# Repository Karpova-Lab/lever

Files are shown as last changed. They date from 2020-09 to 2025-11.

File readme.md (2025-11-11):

# Retractable Lever

This repository contains design files for a retractable lever used in behavioral neuroscience experiments.

Full documentation can be found at https://karpova-lab.github.io/lever/

Feedback and questions can be submitted to [discussions](https://github.com/Karpova-Lab/lever/discussions).

demo gif
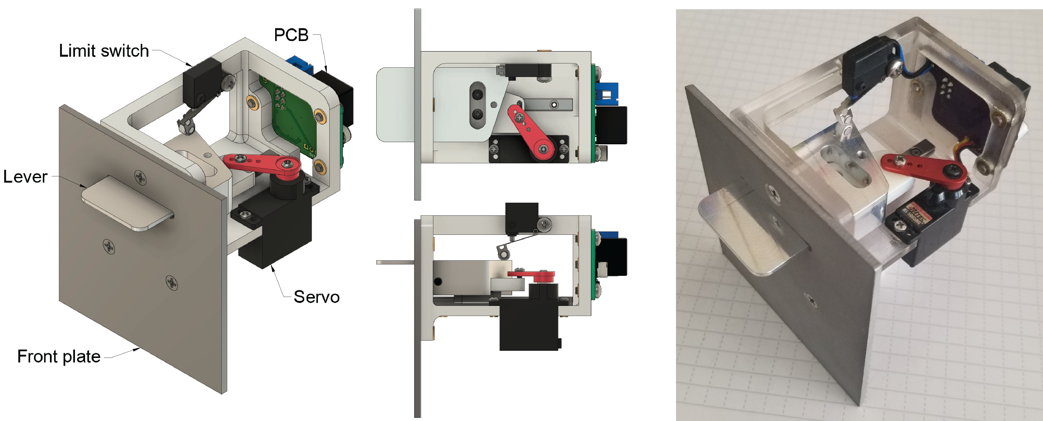
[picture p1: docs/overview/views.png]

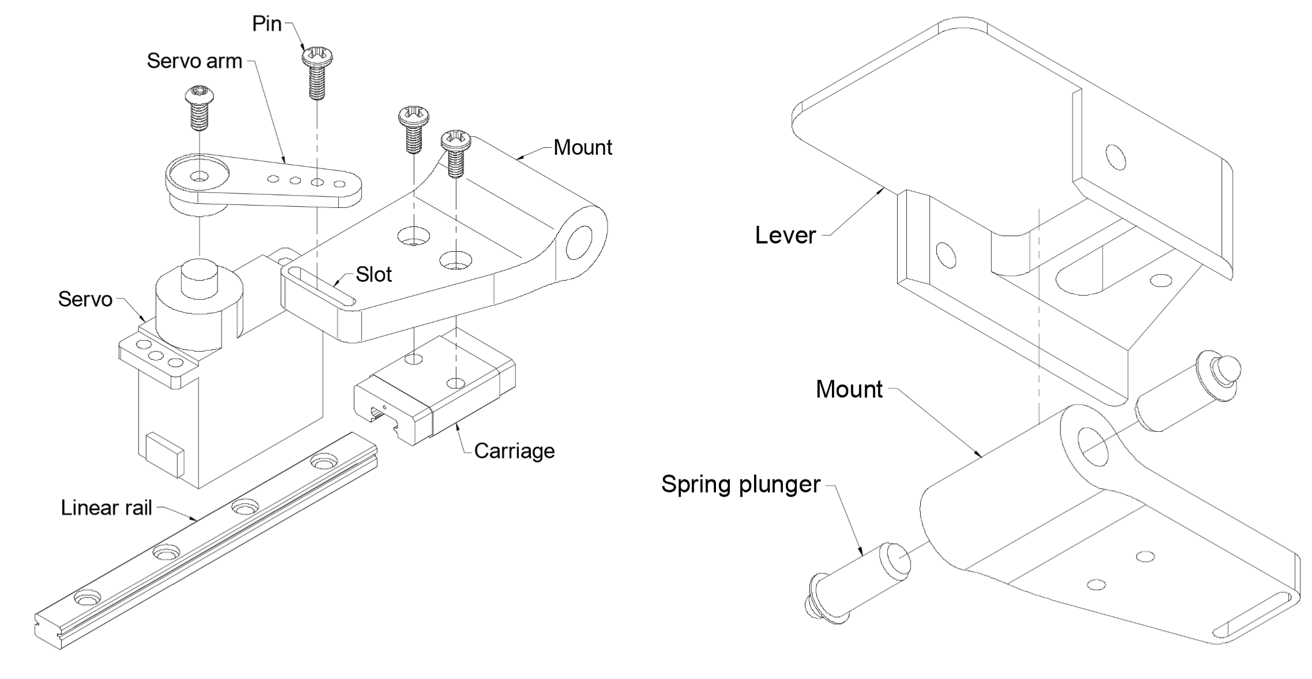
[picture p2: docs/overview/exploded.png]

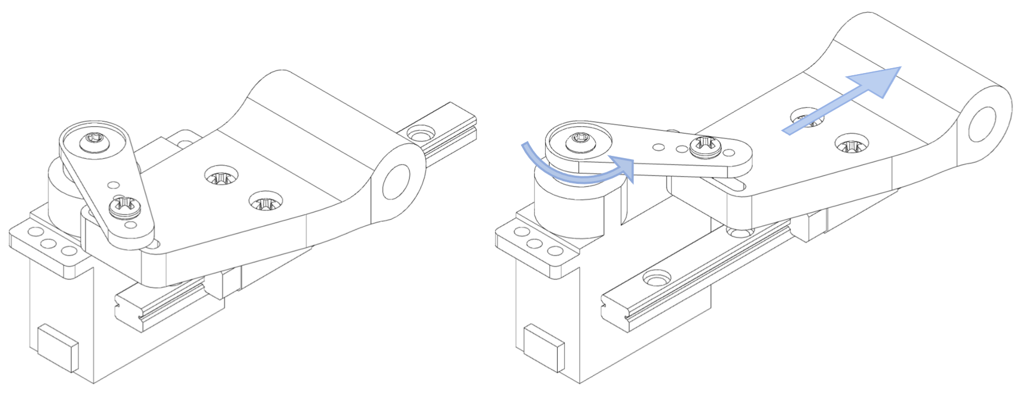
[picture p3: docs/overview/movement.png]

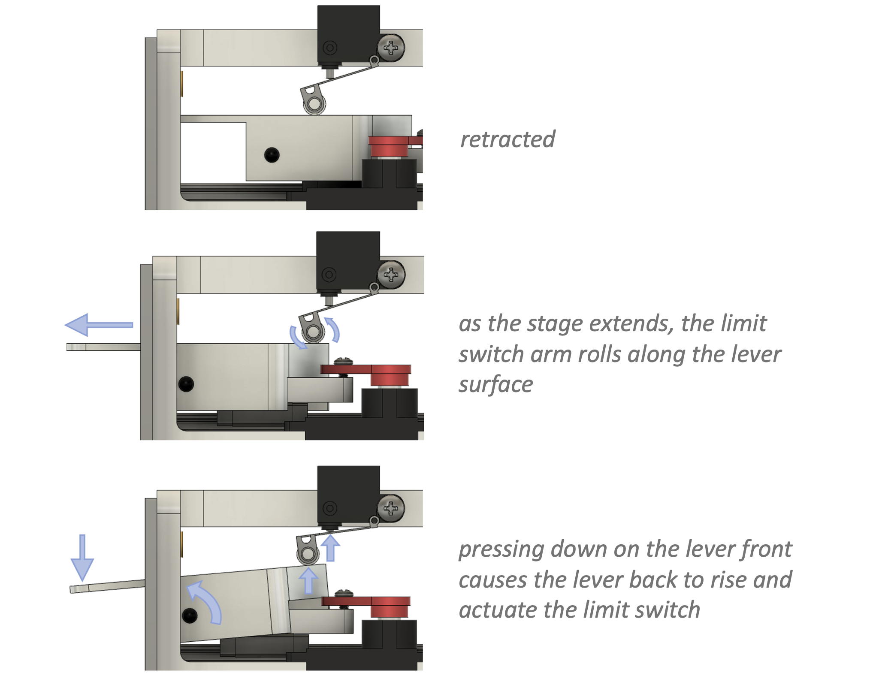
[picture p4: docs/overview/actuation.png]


## License
This project is licensed under the [Janelia open-source hardware license](license_hardare.txt) and [Janelia 3-term BSD open-source software license](license_software.txt).

Please contact [innovation@janelia.hhmi.org](mailto:innovation@janelia.hhmi.org) if you have any questions about licensing or would like to use this project commercially.

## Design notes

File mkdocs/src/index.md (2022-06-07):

# Overview



This is the documentation for building and using a retractable lever.

This project was developed by Andy Lustig in the [Karpova Lab](https://www.janelia.org/lab/karpova-lab) at HHMI's Janelia Research Campus.

## Features

- Receives an input signal to either extend or retract the lever
- Produces an output signal corresponding to the status of the lever (pressed or not pressed)
- [pyControl](https://pycontrol.readthedocs.io/en/latest/user-guide/hardware/#behaviour-ports) compatible
- Fast - 180ms to extend or retract
- Durable - faceplate and lever are made of aluminum and can hold up to abuse from rodent claws and teeth
- Open source - all files are available on [GitHub](https://github.com/Karpova-Lab/nosepoke) and can be modified to meet custom needs

## Diagrams

### Exploded views


<figcaption>(Left) The servo and lever mount interface using a pin and slot mechanism. (Right) The lever rotates about two spring plungers.</figcaption>

### Carriage movement

<figcaption>The rotation of the servo arm is translated into linear movement of the carriage along a guide rail</figcaption>

### Lever function


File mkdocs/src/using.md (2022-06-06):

# Using

## pyControl

This lever works with the [pyControl](https://pycontrol.readthedocs.io/en/latest/) behavior framework. 
Specifically, this means that the RJ45 [pinout](https://pycontrol.readthedocs.io/en/latest/user-guide/hardware/#behaviour-ports) is compatible with pyControl. 
Using an ethernet cable, you can connect the lever to an [original breakout board](https://open-ephys.org/pycontrol/pycontrol)  or a [D-series breakout board](https://karpova-lab.github.io/pyControl-D-Series-Breakout/index.html). 

## Example task

!!! info 
    For the example to work, [:material-file-download: lever_device.py](using/lever_device.py) must be downloaded and placed in your `devices` folder. 
    Then after connecting to you pyboard, use the "config" button to "Load framework".
    This will transfer the device files, including _lever.py, from your computer onto the pyboard microcontroller.

Below is an example task you can run to test the lever. 
The task assumes a lever is connected to **port 1** of your breakout board.

When the task starts, the lever will extend. 
Pressing the extended lever 3 times will cause the lever to retract.
After 1 second, the lever will extend again.
The number of presses required and the duration of the retraction are variables that can be adjusted.

``` python
from pyControl.utility import *
from devices import *
import pyControl.hardware as _h

## uncomment one of the following two lines depending out which breakout board you are using
board = Breakout_1_2()  # original pyboard breakout
# board = Breakout_dseries_1_6()  # d-series pyboard breakout

lever = Lever(board.port_1, lever_event="lever")

states = ["available", "retracted"]
events = ["lever", "extend_again"]

v.press_count___ = 0
v.retract_time_ms = 1000
v.required_presses = 3
initial_state = "available"

def available(event):
    if event == "entry":
        lever.extend()
        v.press_count___ = 0
    elif event == "lever":
        v.press_count___ += 1
        if v.press_count___ == v.required_presses:
            goto_state("retracted")

def retracted(event):
    if event == "entry":
        lever.retract()
        set_timer("extend_again", v.retract_time_ms)
    elif event == "extend_again":
        goto_state("available")
```

For more information on writing your own tasks, refer to the  [pyControl documentation](https://pycontrol.readthedocs.io/en/latest/user-guide/programming-tasks/).

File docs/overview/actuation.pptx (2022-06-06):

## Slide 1

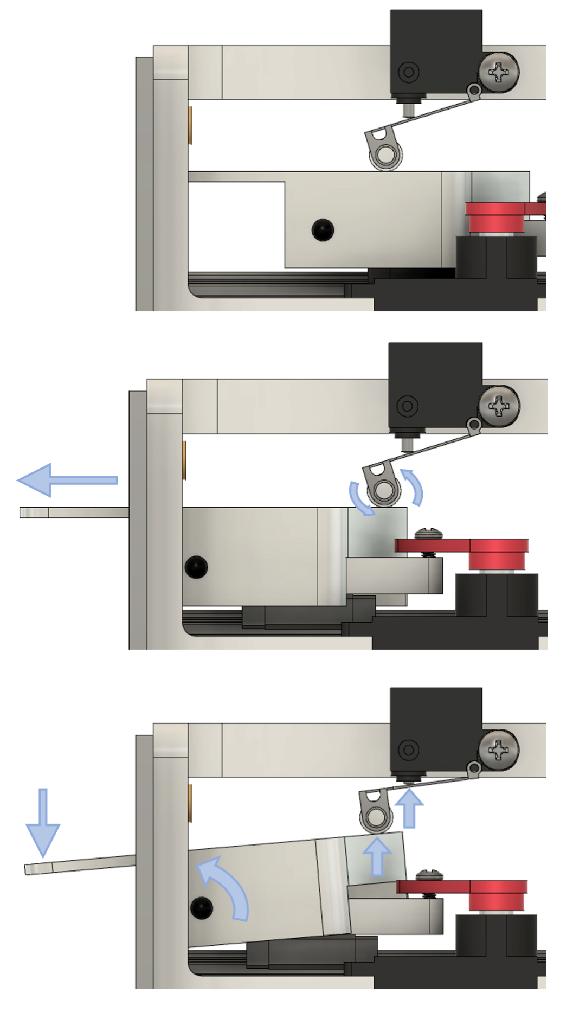
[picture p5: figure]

retracted

as the stage extends, the limit switch arm rolls along the lever surface

pressing down on the lever front causes the lever back to rise and actuate the limit switch

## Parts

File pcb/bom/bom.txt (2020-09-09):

"Qty","Reference","Description","Value/MPN","Purchase Link"
"1","C1","0603 Capacitor","0.1 µF","https://www.digikey.com/products/en?keywords=1276-1258-1-ND"
"1","C2","Capacitor","470 µF","https://www.digikey.com/products/en?keywords=P15094CT-ND"
"1","D1","Indicator LED","Red","https://www.digikey.com/products/en?keywords=160-1447-1-ND"
"1","J1","RJ45 Jack","0855135013","https://www.digikey.com/products/en?keywords=WM3553CT-ND"
"1","R1","0603 Resistor","20KΩ","~"
"1","U1","ATtiny 24 MCU","ATTINY24A-SSUR","https://www.digikey.com/products/en?keywords=ATTINY24A-SSURCT-ND"
"1","X1","ISP Header","75869-331LF","https://www.digikey.com/products/en?keywords=609-5122-ND"

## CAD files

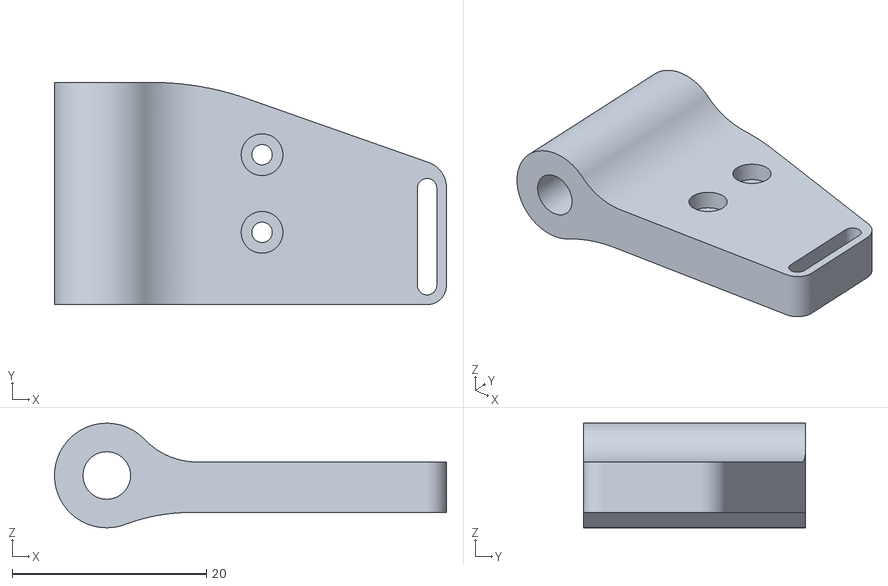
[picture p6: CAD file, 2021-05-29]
docs/building/downloads/carriage.stl
40.4 x 22.9 x 10.8

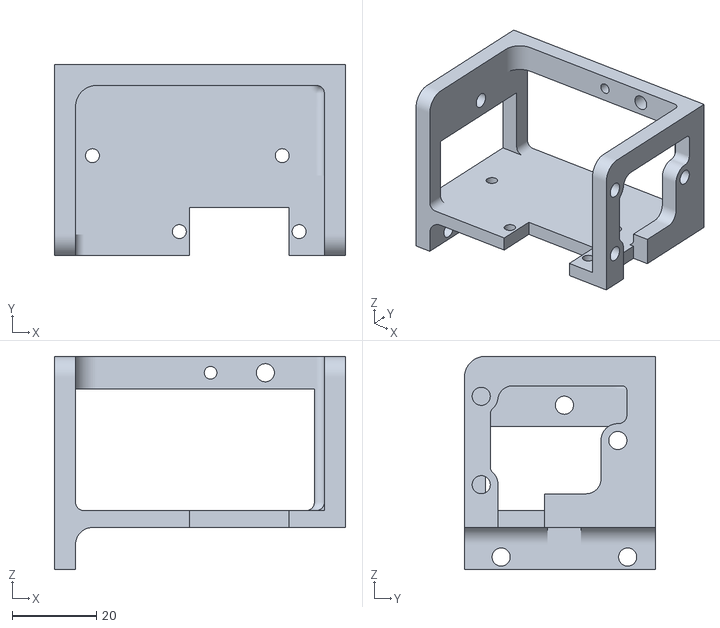
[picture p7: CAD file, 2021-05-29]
mkdocs/src/building/downloads/frame.stl
69.0 x 45.4 x 50.6

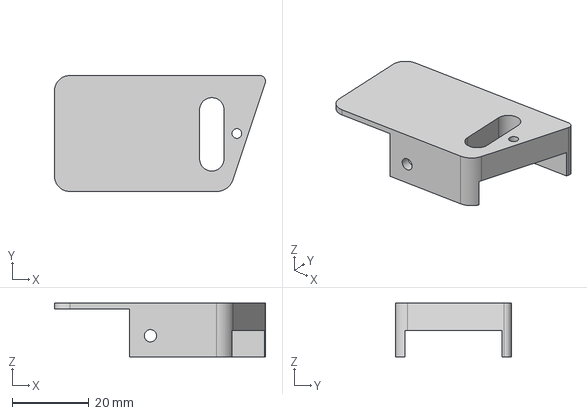
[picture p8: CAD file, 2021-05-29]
mkdocs/src/building/downloads/lever.step
55.0 x 30.2 x 14.0 mm

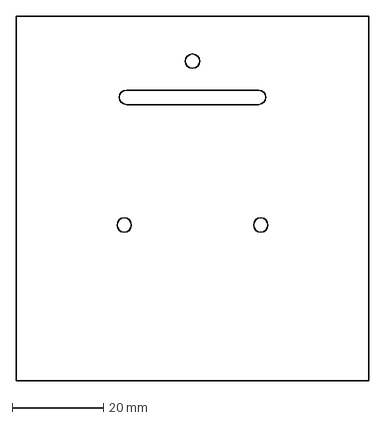
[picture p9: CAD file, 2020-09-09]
docs/building/downloads/front_plate.dxf
77.5 x 80.0 mm

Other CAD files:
docs/building/downloads/lever.stl
mkdocs/src/building/downloads/lever.stl

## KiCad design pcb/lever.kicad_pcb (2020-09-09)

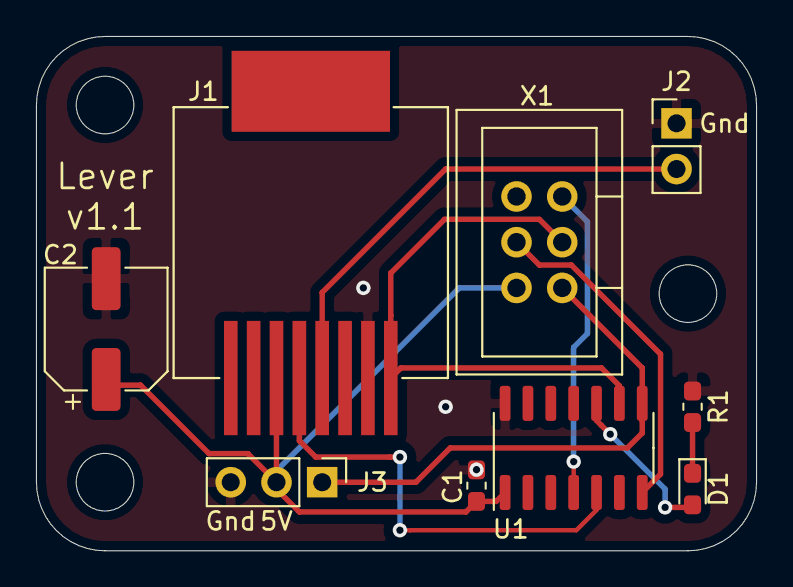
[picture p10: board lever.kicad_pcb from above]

Board: 2 copper layers, 40.0 x 28.6 mm, 12 parts (0 on the bottom side), 10 nets.

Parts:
C1: 0.1µF; C_0603_1608Metric_Pad1.05x0.95mm_HandSolder
C2: 470 µF; CP_Elec_6.3x4.9
D1: LED; LED_0603_1608Metric_Pad1.05x0.95mm_HandSolder
H1, H2, H3: MountingHole; MountingHole_3.2mm_M3
J1: RJ45_pyControl; RJ45_SMD_Vertical
J2: Conn_01x02; PinHeader_1x02_P2.54mm_Vertical
J3: Conn_01x03; PinHeader_1x03_P2.54mm_Vertical
R1: 10KΩ; R_0603_1608Metric_Pad1.05x0.95mm_HandSolder
U1: ATtiny84-20SSU; SOIC-14_3.9x8.7mm_P1.27mm
X1: AVR_ISP

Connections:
/DIO_A: J1.1, U1.9, X1.3
/DIO_B: J1.4, J2.2
/DIO_C: J1.5, U1.5
/GND: C1.1, C2.2, J1.2, J2.1, J3.3, R1.1, U1.14, X1.6
/Vcc: C1.2, C2.1, J1.6, J3.2, U1.1, X1.2
unnamed: D1.1, R1.2
unnamed: D1.2, U1.10
unnamed: J3.1, U1.8, X1.1
unnamed: U1.4, X1.5
unnamed: U1.7, X1.4

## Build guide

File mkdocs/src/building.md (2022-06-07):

# Building

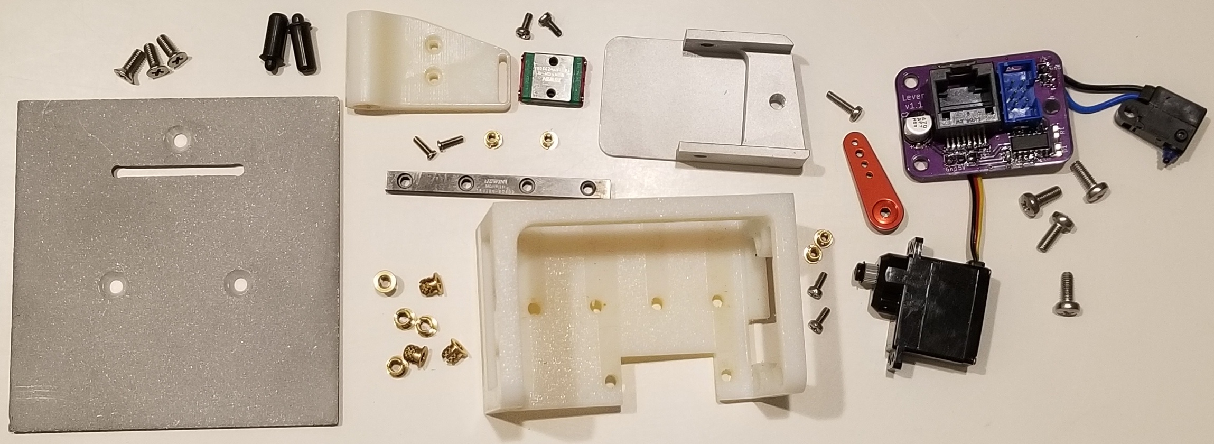
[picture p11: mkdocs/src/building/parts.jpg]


## Hardware

| QTY | Description                | Part Number                                                                                                                                       | Supplier      | 
|-----|----------------------------|---------------------------------------------------------------------------------------------------------------------------------------------------|---------------|
| 2   | Press-fit spring plunger   | [8683A11](https://www.mcmaster.com/8683a11)                                                                                                       | McMaster-Carr | 
| 7   | M3 threaded insert         | [94510A240](https://www.mcmaster.com/94510A240/)                                                                                                  | McMaster-Carr | 
| 3   | M3 x 8 mm flat head screws | [92010A118](https://www.mcmaster.com/92010A118/)                                                                                                  | McMaster-Carr | 
| 4   | M3 x 8 mm pan head screws  | [92000A118](https://www.mcmaster.com/92000a118)                                                                                                   | McMaster-Carr | 
| 4   | M2 threaded insert         | [94510A360](https://www.mcmaster.com/94510a360)                                                                                                   | McMaster-Carr | 
| 2   | M2 x 5 mm screws           | [92000A012](https://www.mcmaster.com/92000a012)                                                                                                   | McMaster-Carr | 
| 1   | 5 x 60 mm linear rail      | [6725K25](https://www.mcmaster.com/6725K25/)                                                                                                      | McMaster-Carr | 
| 1   | 5 mm block/carriage        | [8438K1](https://www.mcmaster.com/8438K1/)                                                                                                        | McMaster-Carr | 
| 1   | Servo                      | [35065S00](https://www.servocity.com/hs-5065mg)                                                                                                   | ServoCity     | 
| 1   | Servo arm                  | [55707](https://www.servocity.com/55707-mini-aluminum-single-arm)                                                                                 | ServoCity     | 
| 1   | Limit switch               | [D2HW-C203MR](https://www.digikey.com/en/products/detail/omron-electronics-inc-emc-div/D2HW-C243MR/2754825?s=N4IgTCBcDaIFoA4CsBmAnAWgHIBEQF0BfIA) | Digi-Key      | 

## 3D printed parts
### Frame
[:material-file-download: frame.stl](building/downloads/frame.stl)

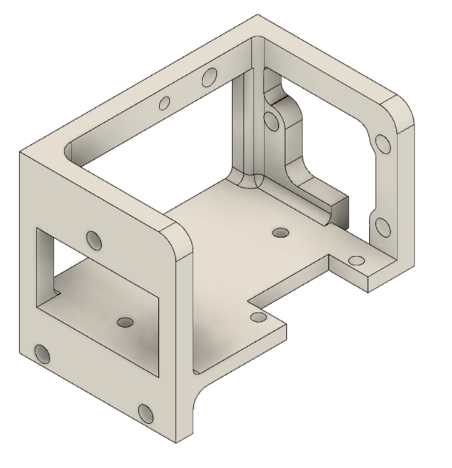
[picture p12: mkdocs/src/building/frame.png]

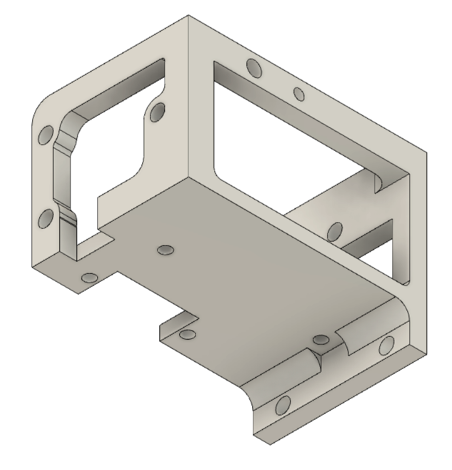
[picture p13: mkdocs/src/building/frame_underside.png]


### Carriage
[:material-file-download: carriage.stl](building/downloads/carriage.stl)

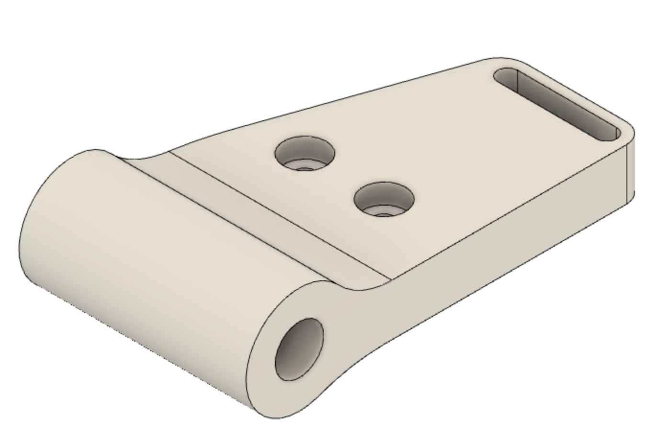
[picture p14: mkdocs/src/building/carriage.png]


## Machined parts
### Lever
[:material-file-download: lever.stl](building/downloads/lever.stl) [:material-file-download: lever.step](building/downloads/lever.step)

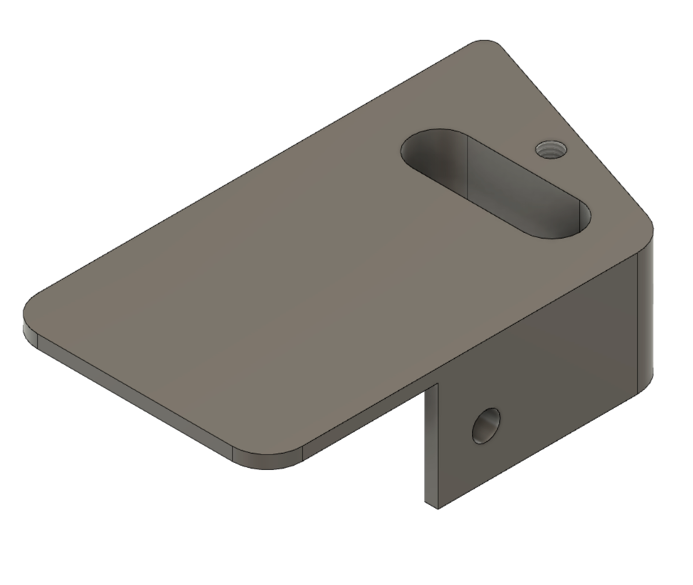
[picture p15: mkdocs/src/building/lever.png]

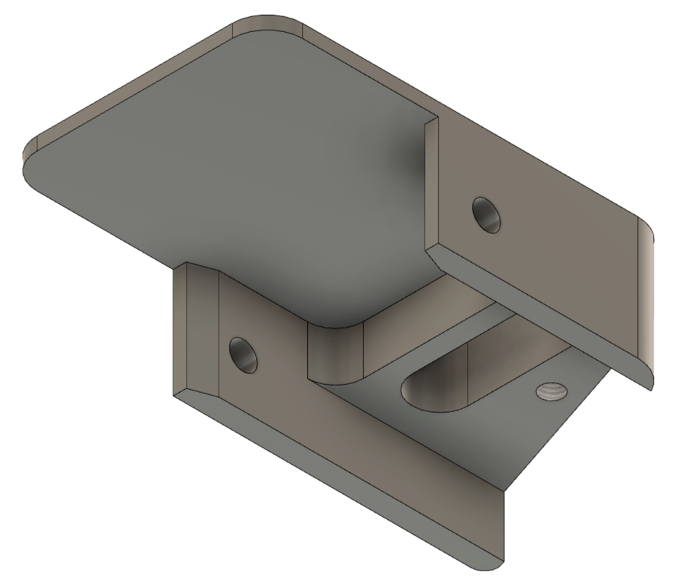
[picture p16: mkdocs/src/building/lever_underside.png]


### Front Plate
[:material-file-download: front_plate.dxf](building/downloads/front_plate.dxf)

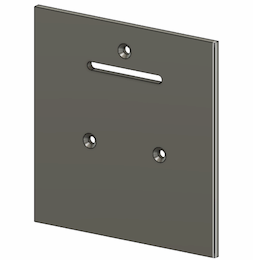
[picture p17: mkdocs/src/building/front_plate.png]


## Electronics

### PCB

PCB source files are on [GitHub](https://github.com/Karpova-Lab/Lever/tree/main/pcb)



=== "layout"
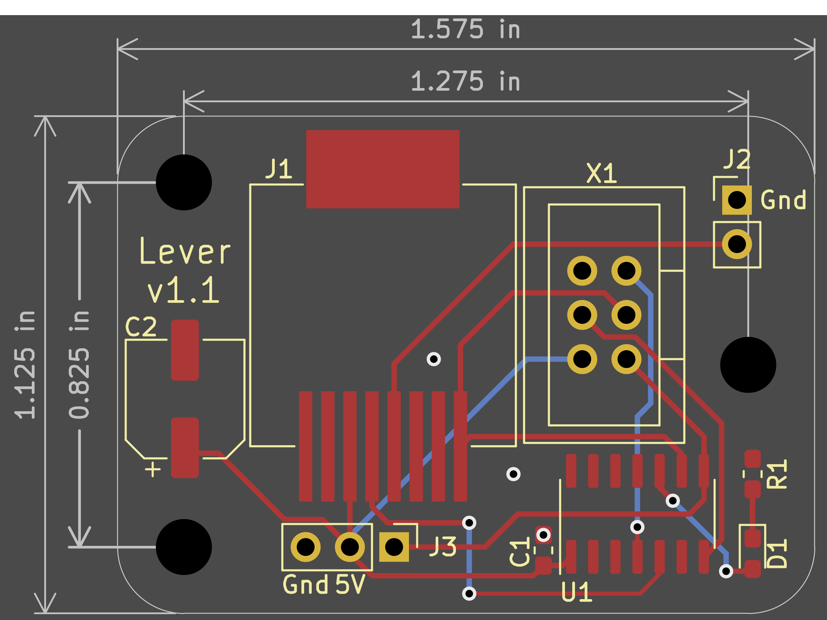
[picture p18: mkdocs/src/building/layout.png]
    
=== "schematic"
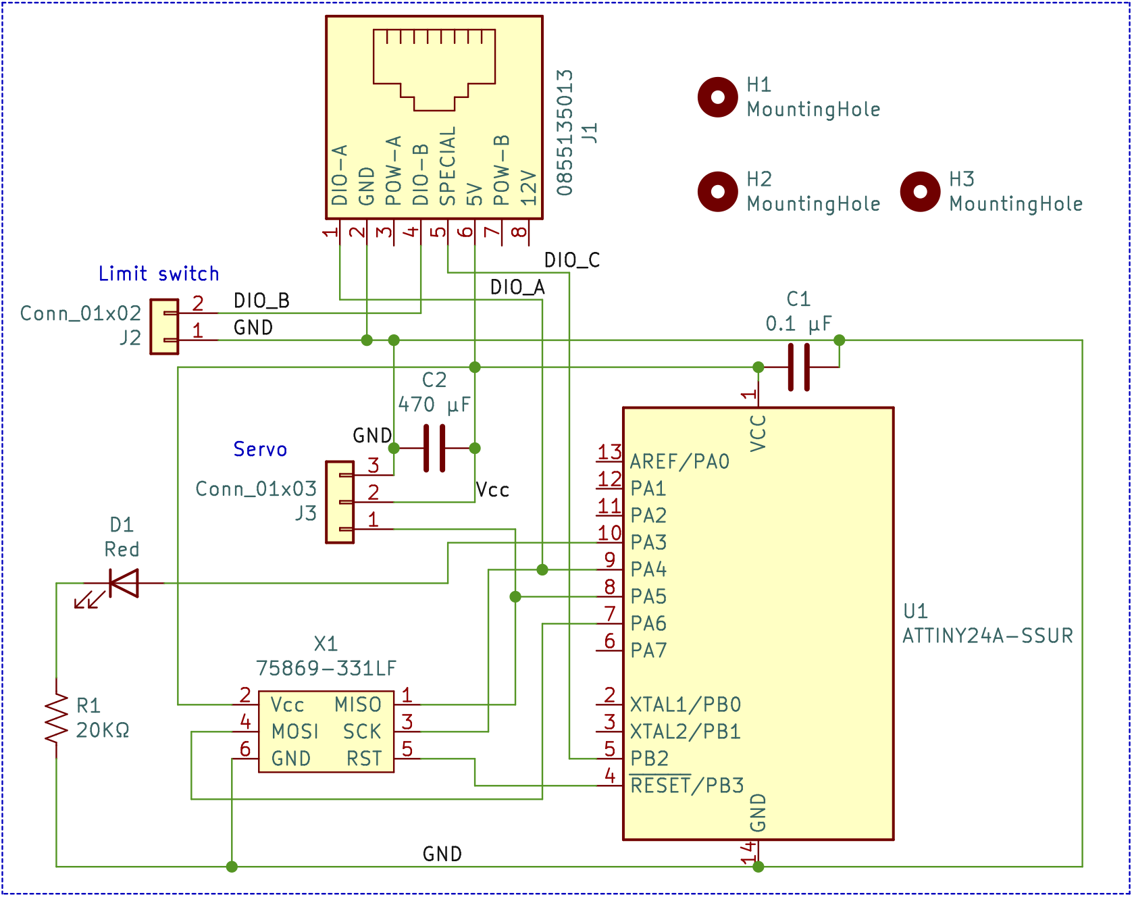
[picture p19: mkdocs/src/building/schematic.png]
    
=== "render"
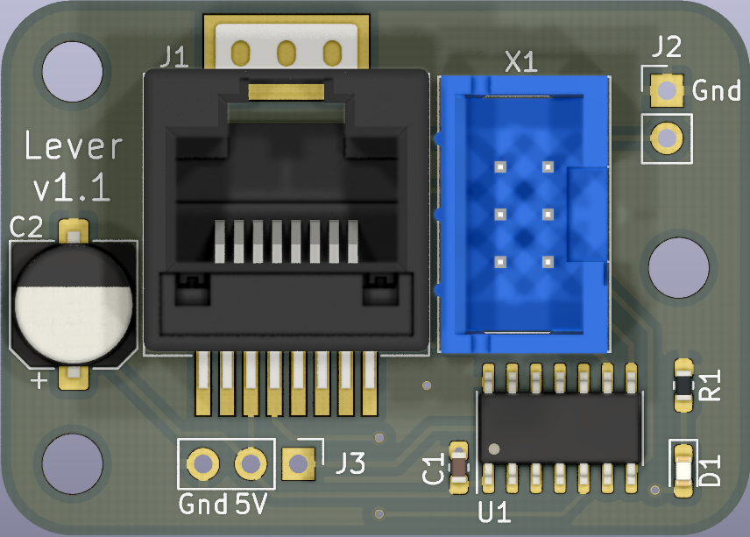
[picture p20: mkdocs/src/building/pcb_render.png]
    

### Bill of Materials

[View interactive BOM](building/ibom.html){ .md-button }

| Qty | Reference | Description            | Value/MPN                                                                                            | 
|-----|-----------|------------------------|------------------------------------------------------------------------------------------------------|
| 1   | C1        | 0603 Capacitor         | [0.1 µF](https://www.digikey.com/products/en?keywords=1276-1258-1-ND)                                | 
| 1   | C2        | Electrolytic Capacitor | [470 µF](https://www.digikey.com/products/en?keywords=P15094CT-ND)                                   | 
| 1   | D1        | Indicator LED          | [Red](https://www.digikey.com/products/en?keywords=160-1447-1-ND)                                    | 
| 1   | J1        | RJ45 Jack              | [0855135013](https://www.digikey.com/products/en?keywords=WM3553CT-ND)                               | 
| 1   | R1        | 0603 Resistor          | [20KΩ](https://www.digikey.com/en/products/detail/stackpole-electronics-inc/RNCF0603BTE20K0/2027042) | 
| 1   | U1        | Microcontroller        | [ATTINY24A-SSUR](https://www.digikey.com/products/en?keywords=ATTINY24A-SSURCT-ND)                   | 
| 1   | X1        | ISP Header             | [75869-331LF](https://www.digikey.com/products/en?keywords=609-5122-ND)                              | 

<!-- ## Assembly

### Required Tools
- Phillips screwdriver
- Soldering iron 

### Instructions
- Place brass inserts into the frame
- Screw down the linear rail -->

## Programming

The ATtiny24 microcontroller is programmed with AVR's ISP (In-circuit Serial Programmer). 
An Arduino can be [used as an ISP](https://www.arduino.cc/en/Tutorial/BuiltInExamples/ArduinoISP) or a purpose build [programmer](https://www.tindie.com/products/nsayer/usb-isp/) can be used. 
The Makefile and C program can be found [here](https://github.com/Karpova-Lab/Lever/tree/main/software/lever). Adjusting the deadband width of the servo requires an [HP-30 servo programmer](https://www.servocity.com/hfp-30-servo-programmer/).

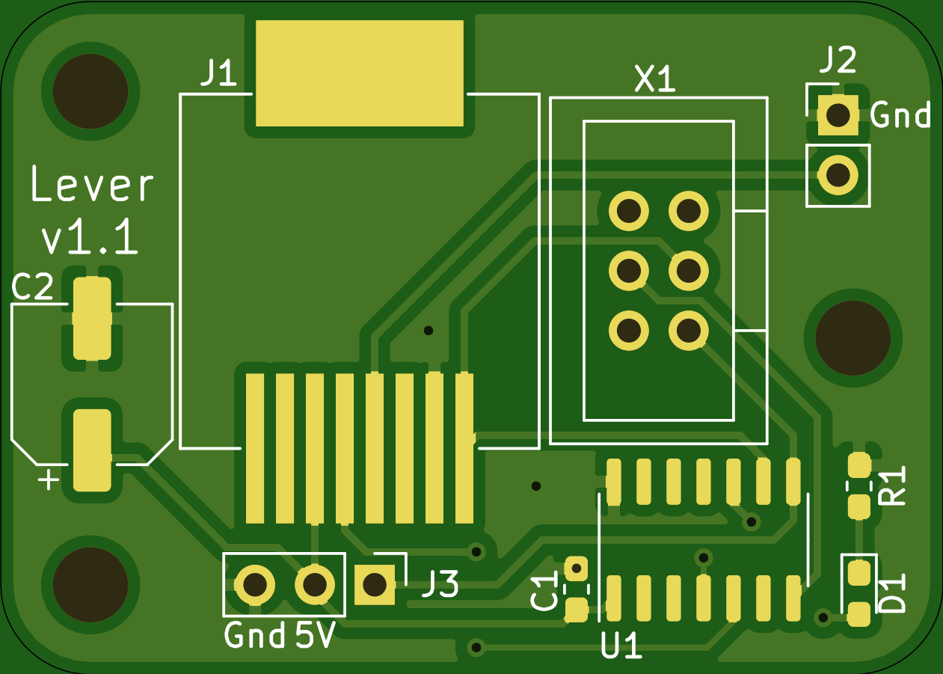
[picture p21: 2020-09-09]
docs/building/pcb_front.png

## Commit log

2020-01-21 pcb v1.0
    [bom.xlsx, lever-B_Cu.gbr, lever-B_Mask.gbr, lever-B_Paste.gbr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]
2020-01-21 pcb v1.1
    [lever-B_Cu.gbr, lever-B_Mask.gbr, lever-B_Paste.gbr, lever-B_SilkS.gbr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]
2020-02-04 can adjust servo position by receiving signal on pyControl's DIO_C. configuration is loaded from and saved to EEPROM
2020-09-09 PCB bom and rendering updates
    [bom.xlsx, lever.kicad_pcb, lever.sch]
2020-09-09 Added 3D and 2D CAD
    [carriage.stl, frame.stl, front plate.dxf, front plate.stl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]
2020-09-09 Added rough draft of docs
    [carriage.stl, frame.stl, front_plate.dxf, hardware bom.xlsx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]
2021-05-25 hugo docs rough draft
    [carriage.stl, frame.stl, front_plate.dxf, hardware bom.xlsx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]
2021-05-29 CAD and software updates
    [carriage.stl, frame.stl, front plate.stl, front_plate.dxf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]
2021-05-29 updated docs
    [carriage.stl, frame.stl, front_plate.dxf, lever.step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]
2022-06-06 convert documentation from hugo to mkdocs
    [carriage.stl, frame.stl, front_plate.dxf, lever.step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]
2022-06-06 lever device file download fix?
2022-06-07 added PCB layout and schematic
